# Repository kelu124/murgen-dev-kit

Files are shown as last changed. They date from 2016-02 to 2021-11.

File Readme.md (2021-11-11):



# The Murgen open-source ultrasound imaging dev-kit 

## What is this ?
 
Getting a home-made open-source ultrasound machine (dev-kit) up and running in your garage / hackerspace / fablab for less than 500$ (want the bolts and nuts of the murgen-based prototype ? Read a more complete [hardware Readme.md](/hardware/Readme.md) and in general the [murgen repo](https://github.com/kelu124/murgen-dev-kit/) ). 

For a full overview of the adventure, visit our [Hackaday page](https://hackaday.io/project/9281-murgen) =)

**For the full documentation of the overaching project, please visit our [full doc](https://kelu124.gitbooks.io/echomods/content/)**

## Getting the rough rough first image

We've got **our first ultrasound image with the murgen board** =) Not a baby, mind you, but at least an echo coming from a part of a fantom (condom filled with agar gel and tapioca balls) in front of the transducer. And we haven't tapped into the full capabilities of the board yet, so it can be improved! Enclosed, the picture of the same fantom, using a commercial, 100k$ ultrasound machine.

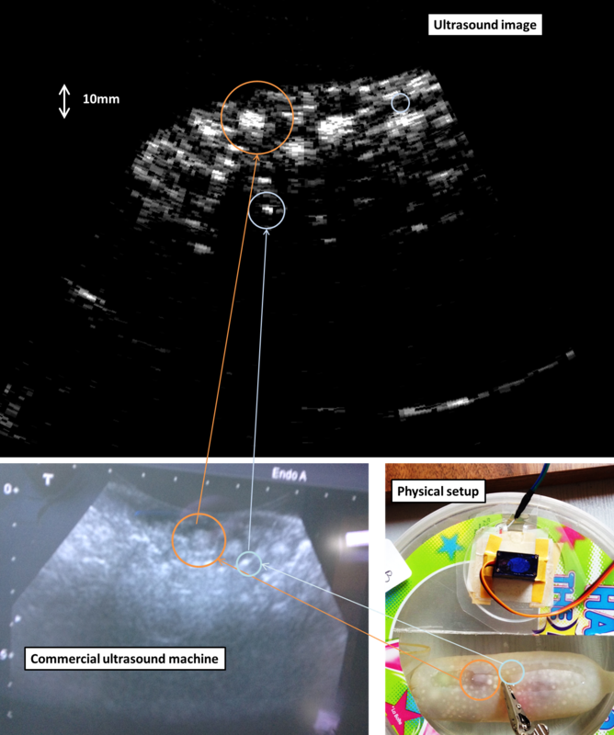
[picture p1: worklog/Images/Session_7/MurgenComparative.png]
A nice image


## Setting up a prototype

### Disclaimers

**Disclaimer #1**: though an engineer, this project is the first of its sort, we never did something related. Bear with us, and the discovery process – we’re happy to learn on the way =)

**Disclaimer #2**: ultrasound raises questions. In case you build a scanner, use caution and good sense!
**Disclaimer #3**: this project is not part of echopen.

### How-to start

Time to get some shopping done !

* Get a murgen dev-kit: 140€ in electronics + PCB. Or 100€ with the components to put on a breadboard =)
* Get a BitScope: 150€
* Get a transducer : 110€ for brand new adaptaed ones, ~100€ for one found on ebay and hacking it
* Get a Trinket Pro / Arduino : 10€
* Get some small electronics (breadboard, cables et al) : 20€
* Misc (Pizza, Beer, and a donation to Murgen): 15€

**_Total spent_: 400€ to 450€**

### Setup
#### Connections

* Connect the BitScope Chan A to Trinket Pin 11, and Chan B to Tests Points2 and 3.
* Connect the trinket pins 12 and 13 to a 5-to-3V convertor (or double invertor), then to the board USPP and USPN pins.
* Bring power to the board (GND, 5V, 3.3V) - the board uses ~150mA at 5V, so you can use a breadboard alim (see IMG_2413 below).

#### Hardware setup presentation

PhysicalSpace

### Software User’s Quick-Start Guide

Just Install the following:

* BitScope BitLib
* python math tools
* Install something to code arduino - ArduinoIDE ?
* Clone the [murgen repo](https://github.com/kelu124/murgen-dev-kit/) 

You're good to go !

### Learn more : the lab log

- [Session 1](/worklog/Session_1.md) : Powering the board, power use, first (bad) trigging and echoes (06 March 2016)
- [Session 2](/worklog/Session_2.md) : Non-controlled pulsing, inverters, better echoes (11 March 2016)
- [Session 3](/worklog/Session_3.md) : Getting controlled pulsing, but width not controlled (15 March 2016)
- [Session 4](/worklog/Session_4.md) : Width of the pulses is getting controlled =) (19 March 2016)
- [Session 4b](/worklog/Session_4b.md) : Simple data visualisation with BitScope (19 March 2016)
- [Session 5](/worklog/Session_5.md) : moving the transducer to get the first image (20 March 2016)
- [Session 6](/worklog/Session_6.md) : ***Getting a clinically usable image*** (28 March 2016)
- [Session 7](/worklog/Session_7.md) : Getting cleaner images - code improvements  (3 April 2016)
- [Session 8](/worklog/Session_8.md) : Comparing acquisition speeds (3 May 2016)
- [Session 9](/worklog/Session_9.md) : Playing with ATL10PV (3 July 2016)
- [A more complete hardware ReadMe](hardware/Readme.md) : Information, and more, with a focus on the electronic part of the project
- [A more complete software ReadMe](software/Readme.md) : Information, and more, with a focus on the code part of the project (arduino, python, and such)

## FAQ

### I want to get to run one

Where should I go? You can peruse a discussion/tutorial with a new user of the board [here](http://kelu124.github.io/murgen-dev-kit/).

### What do I find here?

A full official dev release, including:

* Terms of reference for the project
* Bibliography
* Detailed designed
* Source file for the electronic board
* Source for the Arduino controlling the board
* Source for acquisition, processing and storage of the images
* A full laboratory log

### Typical Application

Playing with a broken transducer in a haribo sweet box to see if you can hack ultrasound scanners.

### Software / Firmware Summary

Up to v1.0, we're still playing with the board, so there's not interface with the BBB.

However, there's a series of tools to play with the board, one of which being the bitscope, a bit more handy than the redpitaya, and though it is less precise, we do have less issues (trigging, memory, ...) with it.

### What is the timeline?

The murgen investigation had started in September 2015, and by the end of November, it had been activated again. 

### Find your way in the folders

 	murgen-dev-kit/				main repo
 	|-- hardware				hardware information on electronics and mecanics
 	|-- software				code to acquire, process and store ultrasound data
 	`-- worklogs				logs froms the lab: our path to a working ultrasound device

* You will find the CHANGES.TXT, CONTRIB.TXT and LICENSE.TXT at the root.
* Schematics are in the ***hardware\Altium\Schematics\PDF*** folder
* Gerbers in in the ***hardware\Gerbers*** folder of course
* Code for the acquisition using bitscope (at first ;) ) is in ***software/***.

# Remaining TODOs

The project's phase is coming to an end! Some ideas, lessons, stuff at our [NextSteps.md](/NextSteps.md)

* Playin with the PRUs, there's [some inspiration there](https://www.element14.com/community/community/designcenter/single-board-computers/next-gen_beaglebone/blog/2013/08/04/bbb--high-speed-data-acquisition-and-web-based-ui)
* There are 5 big projects listed on the [NextSteps.md](/NextSteps.md) document.

# Team

## Acknowledgement

* Thanks to Murgen, Sofian, Amit, Emmanuel, Florent, Bertrand & PHH, Mike in a way, list goes on !
* Thanks to Jerome, Farad, Vincent obviously
* Thanks to echOpen for the environment, wifi and coffee =)

# License

The Murgen project and its prototypes are open hardware, and working with open-hardware components.

Licensed under TAPR Open Hardware License (www.tapr.org/OHL)

Copyright Kelu124 (kelu124@gmail.com ) 2015-2018

[Source](/Readme.md)

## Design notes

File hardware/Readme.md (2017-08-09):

# The Murgen Project
_The hardware design process is fraught with pitfalls, from library component sketchiness, parts availability, erroneous data sheets, underestimates of complexity and long lead times. Designing good hardware on time, on budget and to specifications is like being in a knife fight. Hardware will cut you._

## What is this project?

Today, **we have achieved the electronic design of the kit and are having it made by a PCB Assembly** – someone to actually assemble the probe, and we're waiting for a first prod so that **we can physically test it with our in house transducer**.

That’s cool! And if you want to learn more (apart from this Readme), you can surf the internet and  :

- Read the the [Hackday Blog](https://hackaday.io/project/9281-murgen) of the fork !

### Results ?
#### Setup 

The working place

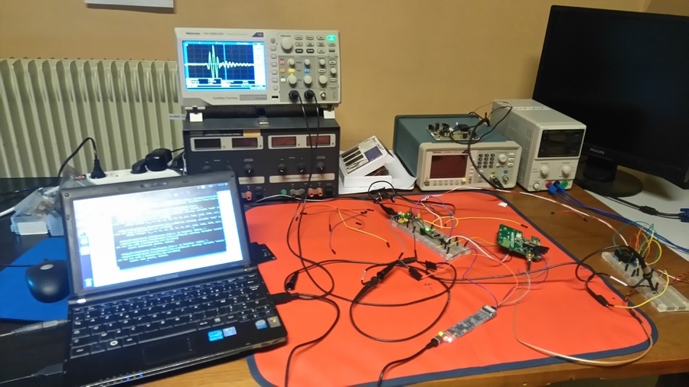
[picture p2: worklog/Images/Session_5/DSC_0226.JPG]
The assembled dev kit


#### Images

A first picture of our baby !

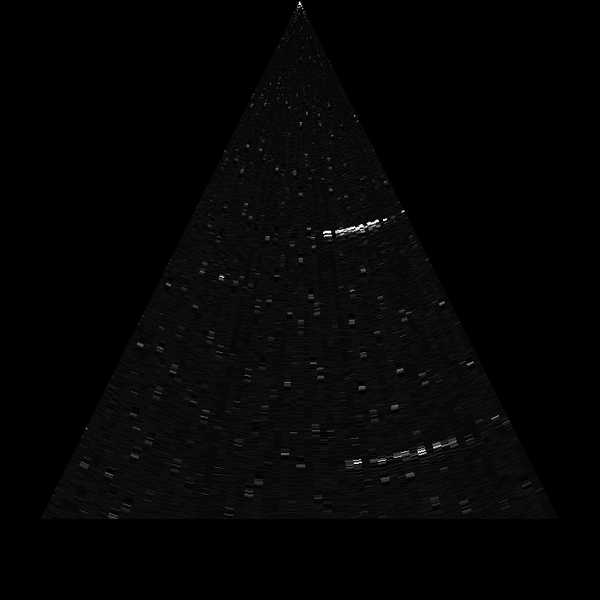
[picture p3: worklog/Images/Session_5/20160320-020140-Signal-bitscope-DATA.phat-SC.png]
An ultrasound image


### Disclaimers
**Disclaimer**: though an engineer, this project is the first of its sort, we never did something related. Bear with us, and the discovery process – we’re happy to learn on the way =)

**Disclaimer #2**: ultrasound raises questions. In case you build a scanner, use caution and good sense!
### Teaser
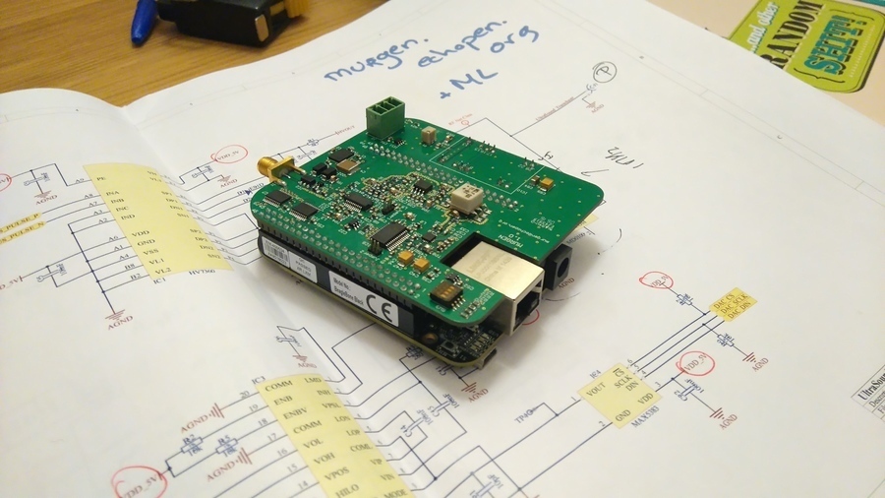
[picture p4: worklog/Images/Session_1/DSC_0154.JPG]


# Folders

    hardware/			main repo
    |-- Altium			the altium files for Murgen -- source files, opening with Altium Designer
    |-- BOM				that's ... well.. for the BOM
    |-- Gerbers			to build the cape
    |-- 3D				for the 3D files of the board	
    |-- tobo			simplified pulser
    `-- goblin			an alternative, in Eagle

You will also find the CHANGES.TXT, CONTRIB.TXT and LICENSE.TXT at the root.
	 
Schematics are in the ***Altium\Schematics\PDF*** folder
	 
# Project introduction

## Brief

**Disclaimer**: this brief ***does not*** rock. It is crappy, but, well, we live to learn.

In October 2015, we were working on a open-source ultrasound imaging device, and had started to get some result. However, we were facing a bottleneck that is data acquisition and transfer.

Roughly, the aim of the device is to excite a 3.5MHz piezo through a 100V or more, 0.2µs, signal to acquire a signal coming from the echoes.

Once it comes back from the transducer, one needs to cap it, amplify it, filter it, apply a time variable gain to the signal, have it get through a high speed ADC (40MHz at least), and serve it to the the processing unit (through PINs, SPI, USB ?), possibly with a CPLD/FPGA (or DSP / microcontroler ?) in between.

As the data we have should have at least 16 imgs / sec, with 64 lines, the rate shall be around 120Mb/s, and to avoid the data transfer bottleneck (see Estimating datarates), we were thinking of leverage the capacities of raspberry (or beaglebone) and such to have shields/capes that can be used and connect through SPI for example to the raspberry where raw data can be processed, and image can be going out, hence a lower rate.

## A bit more context

### The board

The board in itself is not a medical device. The board is a dev kit for the analog part that one could find in any ultrasound probe. It respects the functions and blocks one can find in basically any probe (pulser, TGC, ADC, ..). A main difference is that this board is designed for a single element, and provides so far only a minimal support for the mechanics behind image formation.

Having a single element allows for more space, less density, and to go straight to a regular, though relatively high-speed ADC.

### The Process

None of us had already done an electronic product, so the process in not that of an experienced team, and we're learning on all the fields: writing down an idea, analysing it, structuring it, develop the plans, build it, test it, build the software.. Rince and repeat.

The most challenging part, and somewhere the easiest, will be to allow anyone with little or no experience to replicate our efforts, and to build another copy of the board. Why is that so? With fresh eyes, that's easier to understand what the blocking points could be, what needs to be detailed, and how.

### Debug Sessions

#### Finding the short

The [notes are here](/hardware/murgen-1.0-short-issue.md) (the murgen-1.0-short-issue.md file). We found the bug, two main issues are to be corrected on board v1.1:

* A short on the ADL5511
* The RECOM has to be mounted upside down, as the pin layout were inverted during the design stage

#### Playing with the board

The notes are here, stemming from the work sessions with the board:

- [Session 1](/worklog/Session_1.md) : Powering the board, power use, first (bad) trigging and echoes (06 March 2016)
- [Session 2](/worklog/Session_2.md) : Non-controlled pulsing, inverters, better echoes (11 March 2016)
- [Session 3](/worklog/Session_3.md) : Getting controlled pulsing, but width not controlled (15 March 2016)
- [Session 4](/worklog/Session_4.md) : Width of the pulses is getting controlled =) (19 March 2016)
- [Session 4b](/worklog/Session_4b.md) : Simple data visualisation with BitScope (19 March 2016)
- [Session 5](/worklog/Session_5.md) : moving the transducer to get the first image (20 March 2016)
- [Session 6](/worklog/Session_6.md) : ***Getting a clinically usable image*** (28 March 2016)
- [Session 7](/worklog/Session_7.md) : Getting cleaner images - code improvements  (3 April 2016)
- [Session 8](/worklog/Session_8.md) : Comparing acquisition speeds (3 May 2016)
- [Session 9](/worklog/Session_9.md) : Playing with ATL10PV (3 July 2016)
- [A more complete hardware ReadMe](hardware/Readme.md) : Information, and more, with a focus on the electronic part of the project
- [A more complete software ReadMe](software/Readme.md) : Information, and more, with a focus on the code part of the project (arduino, python, and such)

## Preliminary questions

### Why are we making this?

Because it’s fun, it the first step towards medical open hardware based on ultrasounds, so it’s an element for echOpen !
And because existing hardware doesn’t come in for low-cost, rough uses.

### Who is this for?

This element, comprised of the analog part of ultrasound imaging processing, is aiming hackers, makers, … all who can have fun prototyping a low-cost ultrasound device.

### How will this be used?

This shall be used in conjunction with the mechanical unit (motor, encoder, transducer), and plugged into a small processing unit (aka Raspberry, or BeagleBOne Black for exemple)

### What features does it need to have (now)?

Be able to emit a ultrasound pulse at high voltage, and receive a signal, clean it, detect the envelop and ADC it.

### What features does it need to have (later)?

Shifting envelope detection to software once we’re sure the processing works at “low” rates.

### What are the legacy requirements?

Nothing yet, except a couple of constraints on the use of the tool.

### Who’s going to build this?

Makers, doers, academics, … can use this. But we’d be happy to go with a PCB assembler at first!

### How many do we want to make?

At first, a couple, to prototype it. Once prototyped, this board could be in the hundreds.

### What is the timeline?

**The objective is to get a first functional prototype by February 2015.**

### What are the Goblin and Tobo stuff ?

Those are two alternatives to murgen, in the sense that components may not be the same for goblin, and that tobo is a mini-murgen, limited to the pulser. Goblin is a simpler version, a two-layer one, but we'll need funds to test this one out =)

## Requirements to build the board

### BOM

In the BOM folder !

### At the fab

#### PCB 

A 4-layer PCB.. not so cheap, but at the same time..

#### Fab

Lots around... choose what you want =)

#### Links

PCB Maker:

- seeedstudio.com
- PCBshopper.com

PCBA abroad :

- myropcb
- nortechsys
- SeeedStudio only north america

PCBA in france:

- Quad Ind
- PCB-Pool
- EdgeFlex

### Costs

With the french fab we're working with, costs sum to 160e, and they are split as follows, prices being without taxes:

- PCB : 7.34e (but there are overcosts to produce the masks, ...)
- Components : 143.5e and T1-6T-KK81+ (sold by 10): 9.34 each, but can come down to 140e with some volume.

In this case, assembly is close to 120e.

## Technically

### Principles of echography

Basically, echography means plotting echoes. It means we have to create a sound pulse (2), use a good sensor (2), find a way to transform a 1D signal to a 2D image (3), listen to the echoes coming back, cleaning them and  processing them to create an image the way a bat would do (4), and to transmit them to a display (5). 5 steps.

The present project aims at taking care of (1), (4) and (5) - meaning amm electronics related to the analogic part of the imaging.

### Narrative of the flow

Since we're using a single sensor (not an array of sensor, as those are used in "regular" machines), we don't have the Beamforming parts. The 
sensor is similar to a speaker, in the sense that it can be used to generate an acoustic signal from electricity, and vice versa. The flow is therefore as follows:

- A pulse generator generates a high negative voltage pulse, which is as low as possible and to excite the transducer (or crystal), which will resonate at his central frequency. In our case, this is 3.5MHz, but that depends on the transducer being used.
- A signal will come back through the echoes, the reverberation of the acoustic waves on "obstacles", exciting the transducer, having it generate an electric signal.
- This will be prepared by a switch. Indeed, the signal needs to be separated from the excitation. Excitation being at -150V, the signal coming back will be in mV - and it needs to be isolated.
- The signal usually goes through a LNA - low noise amplifier - to be amplified
- then it's processed by a TGC to compensate for signal attenuation. Indeed, the deeper the echoes come back from, the more attenuated they are, and this needs to be corrected.
- An AAF (Anti-Alias Filte) can be put in between, and in the case of the first Murgen release, we also include an enveloppe detection: indeed, echoes are signals that are coming from a couple of ultrasound periods reflected on interfaces, and what interests us is not (at first) the signal itself, rather the enveloppe of it.
- The "cleaned" signal goes through an ADC to be digitalized
- this is output to buffers, in our case to protect the BBB GPIOs.

### Data rates and key figures

- We're aiming at **128 lines/image** - that may be enough at first 
- at **16 imgs/s**, that's 2048 lines/s
    - That's 488us per line (for everything: 
- Let's image no further than 15.77cm deep.. Why? Because :
    -(15.77 cm x 2) / (154000 cm/s) = 204.805 us 
    -that's 1024 pts at 5MHz
    -That's **204.805 us** per line
    -That's **283.5 us** of idle time - kept for processing, and whatnots
- Final image is therefore **128*1024 px**
    -1024 pts for 15.77cm is 6.49px / mm
    -That's also 2.1Msps on average or 24Mbit/s.. borderline for data transfer on certain systems.

## Discussions

The bottleneck may lie in the data transfers...

### Data rates and Data bus

- 151202: QuadSPI through a dedicated microcontroleur?
- 151201: At 5Msps, 12 bits, shall we use SPI or parallel? 
- 151201: SPI is managed through hardware... parallel, not. Has to be managed from soft. Can be an issue for real time, and to avoid loosing samples.
- 151130: Rather be going onto SPI : QuadSPI? Is that managed by the RPi? Common amongst ADCs ?
- 151207: For high speed data acquisition: about 120Mbits/sec: No SPI port will support such speed…. Only the  Quad version… we can use USB 2.0 HS for such huge movement.  A FPGA or FPGA/RISC MPU combination can be the best  solution. Later, once on RPI, the data can be handled. But for so  perfect measurement of times, and value, only a DSP it’s not enough.  

### Signal detection

- 151129: LTC5507ES6 to filter ? A rajouter!

### ADC and DAC

- 151130: Better ADC at LTC2315-12
- AD7356 (ual, 12-bit, high speed, low power, successive  approximation ADC that operates from a single 2.5 V power  supply and features throughput rates up to 5 MSPS.  
- DAC: a simple DAC i2c 

### Different setups

- 151202: A DSP may be sufficient for our needs: is that the case? 
- 151203: Proposed setup
    - Using a a Main controller - STM32F407 + USB High speed PHY ?? 
    - Analog frontend :  1/4 of AD8264 as LNA and VGA + AD9236 ADC. TGC  can be controlled by internal STM32 DAC - that's max 100-point TGC  calibration curve.  The ADC then could be connected to DCMI interface of  STM32.
    - Transmitter: could be HV Pulser and the TR switch - microchip HV7360 + MD0100,  STHV 748 
- 151209: In  looking at the issue, I think that DSP can be implemented. Of  course,  that comes with the sourcing and a bit of programming, but it  should  work and provide some flexibility. 
- 151112: 
     - it'd be interesting to keep a 100M s/s sampling rate.  
    - wouldn't recommend MD1210 and TC2320 from supertex for the pulse  part. Those have a recovery time that is quite long, and can get easily  damaged - not to mention that they may be obsolete.  
    - Wouldn't recommend two VGAs ... difficult to control, with a high risk of saturation. 

### 151201 : Electronics for all in one chips: AFE (Analog front end)

#### Rationale 

It appears that compoonent MAX2082 from  Maxim's could be a great choice because it integrates everything in one chip (Analog Front End, Pulser, TCG (ou AVG pour eux), T/R Switch, ADC, Filtrage) - maybe better exists ?
Note : Pre-existing chips are 8-channels.

##### Resources

- MAX2082 - Maxim  (Pulser +/- 105 V), TCG (ou VGA) , ADC 50 MSPS and filtering (63$ a piece starting at 1000 units)
https://www.maximintegrated.com/en/products/analog/data-converters/analog-front-end-ics/MAX2082.html
- Several Maxim's Analog Front end  : https://para.maximintegrated.com/en/results.mvp?fam=us_afe
- Pulser - 90 V (16$ a piece starting at 1000 units) : http://www.st.com/web/en/news/n3553d
- A  Texas Instrument Dev Kit : http://www.ti.com/tool/tx-sdk-v1
- Several other Ultrasound Analog Front end (all are 8 channels):  
    - http://www.analog.com/media/en/news-marketing-collateral/product-highlight/AD927x-AD967x-Octal-Ultrasound-AFE-Product-Family.pdf
    - http://www.analog.com/en/products/landing-pages/001/integrated-afe-contains-8-ultrasound-rcv-channels.html
    - http://www.analog.com/en/products/analog-to-digital-converters/ad-converters/ad9675.html
    - http://www.digikey.com/web%20export/supplier%20content/TI_296/mkt/health/afe5809.pdf?redirected=1
    - http://www.ti.com/product/afe5801
- Ultrasound Receiver module (32 channel) (maybe not so cheap) : http://www.cephasonics.com/product/ultrasound-receiver-modules-csm913233

#### Need of a FPGA ?

According to articles and reading, it seems like it will be delicate to proceed without a FPGA for data processing. All "Reference Design" sheets I've read do have a FPGA, or a DSP.... because signals to be processeed are IMHO too fast for a µC.

#### Microcontroler

- Microchip - a µC PIC24FJ128GC010 - ADC, 12 bit, 10 MSPS : http://www.microchip.com/wwwproducts/Devices.aspx?product=PIC24FJ128GC010
- and its dev board at 100$: http://www.microchip.com/Developmenttools/ProductDetails.aspx?PartNO=DM240015
- ST ant its ADC 12 bit 5 MSPS  µC STM32F334R8: http://www.st.com/web/en/catalog/mmc/FM141/SC1169/SS1576/LN1531/PF258875#
- with its dev board at 10 € : http://fr.farnell.com/stmicroelectronics/nucleo-f334r8/carte-dev-32-bits-stm32f334r8/dp/2424210
- Analog Device has a reference list µC  : 
http://www.analog.com/en/products/processors-dsp/analog-microcontrollers/8052-core-products.html
- At analog device, the best seems to be ADSP-CM40XF with a 16 bit ADC at 2,3 MSPS: http://www.analog.com/en/products/processors-dsp/cm4xx-mixed-signal-control-processors/adsp-cm403f.html#product-overview  and its 2 dev boards:
 - http://fr.farnell.com/analog-devices/adzs-cm408f-ezlite/kit-d-eval-ez-kit-lite-adsp-cm408f/dp/2367988?CMP=GRHS-1000059
 - http://fr.farnell.com/analog-devices/adzs-cm403f-ezlite/kit-d-eval-ez-kit-lite-adsp-cm403f/dp/2367987?CMP=GRHS-1000059
- I also found some MCU with an internal ADC and a good rate wich seems interesting : http://www.analog.com/en/products/processors-dsp/analog-microcontrollers/8052-core-products.html and http://www.microchip.com/Developmenttools/ProductDetails.aspx?PartNO=DM240015

### Forks

#### Constraints

- 151124: The tech milestone was on Nov 24th '15 -  and we need to have something by mid Feb' 16.

#### YDO ideas

- 151125: I'm pretty sure that it's impossible that a microcontroler, raspberry or beaglebone can process this data at a speed above 5Msps.  Most of ADCs have a SPI interface, with a 12-bit ADC at 5Msps we'd need a SPI at more than 60Mbps - not everything can do ! In such a case, a DSP or a FPGA is a must-have.

#### LJO/FKA cape

- 151124: let's play with the BBB PRU's and develop a analog+ADC cape.

### HV Supply

HV-supply is going to introduce noise in the circuit.. therefore, a home-made booster was not selected, especially when going at 100V+. We had to options to consider:

- Using a **MAX1711** in [Jatin Sharma thesis](https://www.duo.uio.no/handle/10852/47813), he goes from 12V to 180V. Gerbers and schematics are included in his master).  The board was separated from the rest of the design, to avoid any pickup/noise.
- We have tried the **R05-100B** - a tad more simple, and based on 5V, so easier for us (5V -> 120V).  Schematics are simple, introducing only a couple of capacities.

### Electronics

So far, the key issue is a compromise in terms of data output. It's interesting to see how to interface such data rates to a processing and display unit.

### Setup

#### Jumper 1

This one represents the fixed Gain for the TGC. An extra 18 dB is always handy!

#### Jumper 2

todo

#### ADC Clock:

The 4 options switch allows for a sampling frequency range of choices:

|  R1 |  R2 |  R3 |  R4 | Rset Value | Clock Frequency |
|:---:|:---:|:---:|:---:|:----------:|:---------------:|
|  1  |  2  |  3  |  4  |     Ohm    |      [MHz]      |
| OFF | OFF | OFF | OFF |   Invalid  |     Invalid     |
| OFF | OFF | OFF |  ON |  100000,0  |       1,0       |
| OFF | OFF |  ON | OFF |   40200,0  |       2,5       |
| OFF | OFF |  ON |  ON |   28673,3  |       3,5       |
| OFF |  ON | OFF | OFF |   27400,0  |       3,6       |
| OFF |  ON | OFF |  ON |   21507,1  |       4,6       |
| OFF |  ON |  ON | OFF |   16294,1  |       6,1       |
| OFF |  ON |  ON |  ON |   14011,1  |       7,1       |
|  ON | OFF | OFF | OFF |   20000,0  |       5,0       |
|  ON | OFF | OFF |  ON |   16666,7  |       6,0       |
|  ON | OFF |  ON | OFF |   13355,5  |       7,5       |
|  ON | OFF |  ON |  ON |   11781,9  |       8,5       |
|  ON |  ON | OFF | OFF |   11561,2  |       8,6       |
|  ON |  ON | OFF |  ON |   10363,1  |       9,6       |
|  ON |  ON |  ON | OFF |   8978,9   |       11,1      |
|  ON |  ON |  ON |  ON |   8239,1   |       12,1      |

## Parts, ICs selection (and critical specs)
 
### HV7360:  High Speed, ±100V 2.5A, Two or Three Level Ultrasound Pulser

* High density integration AC coupled pulser
* 0 to ±100V output voltage
* ±2.5A source and sink minimum pulse current
* Up to 35MHz operating frequency
* 2.0ns matched delay times
* 2.5, 3.3 or 5.0V CMOS logic interface
* Low power consumption and very simple to use

HV7360 is a high voltage, high-speed, pulse generator with built-in, fast return to zero damping FETs. This high voltage and high-speed integrated circuit is designed for portable medical ultrasound image devices, but can also can be used for NDT and test equipment applications.

The HV7360 consists of a controller logic interface circuit, level translators, AC coupled MOSFET gate drivers and high voltage and high current P-channel and N-channel MOSFETs as the output stage. The peak output currents of each channel are guaranteed to be over ±2.5A with up to ±100V of pulse swing. The AC coupling topology for the gate drivers not only saves two floating voltage supplies, it also makes the PCB layout easier.

### Protection: MD0100 Datasheet - HV Protection T/R Switch

* Up to ±100V input voltage protection
* Low on resistance - 15O typical
* Fast switching speed
* Effectively, a simple two terminal device
* No external supplies needed

MD0100 is a high voltage, two terminal, bi-directional, current-limiting protection device. The two terminals are interchangeable. It is designed to protect a low noise receiver from the high voltage transmit pulses in ultrasound applications and is commonly referred to as a T/R (transmit and receive) switch. The MD0100 can be considered as a normally closed switch with a typical switching resistance of 15O that allows small signals to pass.

Once the voltage drop across the two terminals exceeds a nominal value of ±2.0V, the device will start to turn off. In the off state, the MD0100 can withstand up to ±100V across its terminals.

A small amount of current, typical of 200µA, is allowed to flow through.
 
### TGC : AD8331 (Single VGA with Ultralow Noise Preamplifier and Programmable RIN)

* Ultralow noise preamplifier
* 3 dB bandwidth: 120 MHz
* Low power: 125 mW/channel
* Wide gain range with programmable postamp (-4.5 dB to +43.5 dB in LO gain mode, 7.5 dB to 55.5 dB in HI gain mode) – we can use this with the corresponding on-board jumper
* Low output-referred noise: 48 nV/vHz typical
* Active input impedance matching
* Optimized for 10-bit/12-bit ADCs : perfect for us
* Selectable output clamping level
* Single 5 V supply operation : ideal for a 5V board supply!

The AD8331 is a single channel, ultralow noise, linear-in-dB, variable gain amplifier (VGA). Optimized for ultrasound systems, it is usable as a low noise variable gain element at frequencies up to 120 MHz.

Included is an ultralow noise preamplifier (LNA), an X-AMP® VGA with 48 dB of gain range, and a selectable gain postamplifier with adjustable output limiting. The LNA gain is 19 dB with a single-ended input and differential outputs. Using a single resistor, the LNA input impedance can be adjusted to match a signal source without compromising noise performance.

The 48 dB gain range of the VGA makes these devices suitable for a variety of applications. Excellent bandwidth uniformity is maintained across the entire range. The gain control interface provides precise linear-in-dB scaling of 50 dB/V for control voltages between 40 mV and 1 V. Factory trim ensures excellent part-to-part and channel-to-channel gain matching. Differential signal paths result in superb second- and third-order distortion performance and low crosstalk.

### TGC  Control : SPI DAC : MAX5383

Controls the TGC
* 8-Bit Resolution in a Miniature 6-Pin SOT23 Package
* Less than 1µA Shutdown Mode
* Low-Glitch Power-On Reset to Zero DAC Output
* 3-Wire SPI/QSPI/MICROWIRE-Compatible Interface : perfect for a SPI interface
* Low 230µA (max) Supply Current

The MAX5383 low-cost, 8-bit digital-to-analog converters (DACs) in miniature 6-pin SOT23 packages have a simple 3-wire, SPI™/QSPI™/MICROWIRE™-compatible serial interface that operates up to 10MHz. The MAX5383 has an internal +2V reference and operates from a +2.7V to +3.6V supply.

The MAX5383 require an extremely low supply current of only 150µA (typ) and provide a buffered voltage output. These devices power up at zero code and remain there until a new code is written to the DAC registers. This provides additional safety for applications that drive valves or other transducers that need to be off on power-up. The MAX5383 include a 1µA, low-power shutdown mode that features software-selectable output loads of 1kO, 100kO, or 1MO to ground.

### Analog envelop detection: ADL5511 - DC to 6 GHz ENVELOPE AND TruPwr™ RMS Detector

* Envelope tracking RF detector with output proportional to input voltage
* No balun or external tuning required
* Input power dynamic range of 47 dB
* Input frequency range from dc to 6 GHz
* 130 MHz envelope bandwidth
* Envelope delay: 2 ns
* Single-supply operation: 4.75 V to 5.25 V

The ADL5511 is an RF envelope and TruPwr™ rms detector. The envelope output voltage is presented as a voltage that is proportional to the envelope of the input signal. The rms output voltage is independent of the peak-to-average ratio of the input signal.
The rms output is a linear-in-V/V voltage with a conversion gain of 1.9 V/V rms at 900 MHz. The envelope output has a conversion gain of 1.46 V/V at 900 MHz and is referenced to an internal 1.1 V reference voltage, which is available on the EREF pin.
The ADL5511 can operate from dc to 6 GHz on signals with envelope bandwidths up to 130 MHz.

### ADC : AD9220 - Complete 12-Bit, 10.0 MSPS Monolithic A/D Converter

* Monolithic 12-Bit A/D Converter Product Family
* Flexible Sampling Rates: 1.5 MSPS, 3.0 MSPS, and 10 MSPS
* Single +5 V Supply
* Out-of-Range Indicator
* 28-SOIC and 28-SSOP

The AD9221/AD9223/AD9220 combine a low cost, high speed single-CMOS process and a novel architecture to achieve the resolution and speed of existing hybrid and monolithic implementations at a fraction of the power consumption and cost. Each device is a complete, monolithic ADC with an on-chip, high performance, low noise sample-and-hold amplifier and programmable voltage reference. An external reference can also be chosen to suit the dc accuracy and temperature drift requirements of the application. The devices use a multistage differential pipelined architecture with digital output error correction logic to provide 12-bit accuracy at the specified data rates and to guarantee no missing codes over the full operating temperature range.

The input of the AD9221/AD9223/AD9220 is highly flexible, allowing for easy interfacing to imaging, communications, medical, and data-acquisition systems. A truly differential input structure allows for both single-ended and differential input sample-interfaces of varying input spans. The sample-and-hold (SHA) amplifier is equally suited for both multiplexed systems that switch full-scale voltage levels in successive channels as well as sampling single-channel inputs at frequencies up to and beyond the Nyquist rate. Also, the AD9221/AD9223/AD9220 is well suited for communication systems employing IF Down Conversion since the SHA in the differential input mode can achieve excellent dynamic performance far beyond its specified Nyquist frequency2.

A single clock input is used to control all internal conversion The digital output data is presented in straight binary format. An out-of-range (OTR) signal indicates an flow condition which can be used with the most significant bit to determine low or high overflow.
 
### Buffers: 74AC541MTC

* Signal isolation is of high value for measurements at this precision (12bit)

The 74AC541 and 74ACT541 are octal buffer/line drivers designed to be employed as memory and address drivers, clock drivers and bus oriented transmitter/ receivers.
 
# Using the Murgen board

## Software / Firmware Summary

Up to v1.0, we're still playing with the board, so there's not interface with the BBB.

However, there's a series of tools to play with the board, one of which being the bitscope, a bit more handy than the redpitaya, and though it is less precise, we do have less issues (trigging, memory, ...) with it.

## Typical Application

Playing with a broken transducer in a haribo sweet box to see if you can hack ultrasounds.

## User’s Quick-Start Guide

- Install 
    - BitScope BitLib
    - python math tools
    - something to code arduino
- Clone this repo

You're good to go !

# Others

## Goodies 
Check out [oldTobo](/hardware/tobo/) -- an stand-alone pulser/receiver board and [oldGoblin](/hardware/goblin/) for an alternative version.

## People ! 

### Acknowledgement

* Thanks to echOpen =)
* Thanks to Jerome, Farad, Vincent obviously
* Murgen, Sofian, Amit, Emmanuel, Florent, Bertrand & PHH, Mike in a way, list goes on !

# License

Licensed under TAPR Open Hardware License (www.tapr.org/OHL)

Copyright Kelu124 (kelu124@gmail.com ) 2015-2016

# Bibliography

## FPGA-related bibliography

- Structuring a whole ultrasound system on a board: an excellent thesis from P. Levesques (Kyvox),  File:2011 PhilippeLevesque.pdf. 
- A first corresponding article: File:Real-Time Hand-Held Ultrasound Medical-Imaging Device Based on a New Digital Quadrature Demodulation Processor.pdf
- the second corresponding article: File:Novel Low-Power Ultrasound Digital Preprocessing Architecture for Wireless Display.pdf
- Hardware-Software Partitioning of Digital Signal Processing in Ultrasound Medical Devices a Case Study : File:Hardware-Software Partitioning of US probes.pdf
 - File:A Single FPGA-Based Portable Ultrasound Imaging System for Point-of-Care Applications.pdf
 - File:Low-Cost, High-Speed Back-End Processing System for High-Frequency Ultrasound B-Mode Imaging.pdf
- Extremely interesting too,  iPHONE ULTRASOUND By Jonathan Adam, Adam Keen, Dean Santarinala  and File:project2_presentation.pdf their presentation

## Key general articles (base of inspiration for our dear Emile)

- A single monoelement, low-cost ophtalmic probe using a piezo motor : File:Carotenuto ophtalmic prob.pdf : an excellent article. 
- A single monoelement, low-cost USB probe using a CPLD + microcontroller File:Richard low cost probe.pdf, including a great diagram block of the USB probe 
- Saijo USB work : Development of an ultra-portable echo device connected to USB port : Resource: File:2004 Development of an ultra-portable echo device connected to USB port.pdf
- A Software-Based Ultrasound System for Medical Diagnosis by Samir Ram Thadani File:1997 These MIT Thadani.pdf : an excellent introduction the overall design of a US probe design dating back from 1997. 
- Data processing and transfer in echography : File:Design of an Open-Architecture Ultrasound Acquisition System for Real-Time Processing and Control.pdf
- Transducer parameters: File:A focussed transducer-scatterer model for ultrasonic reference st.pdf

## Other

- Projet étudiant, réalisation d'un échographe de poche pour Iphone (très intéressant et très instructif...) : https://courses.engr.illinois.edu/ece445/getfile.asp?id=5167
- White paper de Xilinx : portable ultrasound system : http://www.xilinx.com/support/documentation/white_papers/wp378-Xilinx-in-Portable-Ultrasound.pdf
- Quelques Notes d'applications intéressantes de chez Maxim's :
https://www.maximintegrated.com/en/app-notes/index.mvp/id/5765
 https://www.maximintegrated.com/en/app-notes/index.mvp/id/5553
- Note d'application de chez ST sur "Ultrasound Imaging" :
 - http://www.st.com/web/en/catalog/apps/SE410/AS430/AC404
 - http://www.st.com/web/en/catalog/apps/SE410/AS430/AC404#
- Pulser TI avec Applcation Note d'une solution complète avec des composants TI :
 - http://www.ti.com.cn/cn/lit/ds/symlink/lm96550.pdf

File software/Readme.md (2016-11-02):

# Software Readme (Bitscope Version)

## Contents of the folder 

### Some files

* All example files are compressed and thumbs created in [the example folder](/software/examples/Readme.md)
* For the convention in files format, [the data files specs are in](/software/examples/Specs.md)

### Some software

* AcquireImage.py acquires the images, stores them in pairs of log files
* CreateImage.py creates the .data file from the log files
* CreateCSV.py creates the .csv file from the log files
* CreateSC.py creates the .png files (Scan Conversion) using a nearest neighbour algorithm, from the .data files
* CreateSC-4T.py creates the .png files (Scan Conversion) using the 4 nearest neighbours to determine the pixel value, from the .data files
* TrinketProCode is the code for the Arduino Trinket Pro.
* BatchImage is a shell script to automate the creation of images properly

### Some files
* The examples.tar.bz2 contains quite a lot of raw images, to be processed by CreateImage.py . There should be around 200Mo of raw images packed in this 4Mo archive.
* The [examples](/software/examples/) repository, and its [Readme](/software/examples/Readme.md),  contains some raw images, along with a table, and the [Specs](/software/examples/Specs.md)) for the data format.
* There's an additional folder for CSV images at [examples](/software/examples_csv/)

# Installing BitScope

## Setting up bitscope tools for Ubuntu, using BS05 (Bitscope Micro)	

1. Installation : install all deb/ .deb files (dpkg -i install_files/*.deb), starting with bitscope-link.
2. Follow the https://www.raspberrypi.org/forums/viewtopic.php?f=32&t=122636 instructions

```
 $ sudo unzip python-bindings-2.0-DC01L.zip -d /usr/share/doc/bitscope-library/examples/python/
 $ cd /usr/share/doc/bitscope-library/examples/python/
 $ cd /usr/share/doc/bitscope-library/examples/python/python-bindings-2.0-DC01L/
 $ sudo python setup-bitlib.py install
```
Compilation fails? To do that we discover that we should do this:
```
 $ sudo BASECFLAGS="" OPT="" CFLAGS="-O3" python setup-bitlib.py install
```
This should work and you should see:
```
 $ python test-bitlib.py 
 Starting: Attempting to open one device...
  Library: 2.0 FE26B (Python DC01L)
     Link: USB:/dev/ttyUSB0
 BitScope: BS000501 (YK26VX18)
 Channels: 10 (2 analog + 8 logic)
    Modes: FAST DUAL MIXED LOGIC STREAM
  Capture: 12288 @ 40000000Hz = 0.000307s (LOGIC)
   Offset: +2.917V to -6.217V
      POD:  9.20V  5.20V  3.50V  1.10V
  Data(5): 1.725000, 1.725000, 1.760937, 1.760937, 1.725000
 Finished: Library closed, resources released.
```

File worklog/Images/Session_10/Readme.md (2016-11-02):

## Testing the ATL3 probe

8h and ... minutes give:

* 37: end of the aquarium (motor: 2.3V)
* 38: itoo
* 39: deeper

* 40: Motor at 5.30V (170mA)
* 41: Motor at 10.3V (300mA)

* 46: Self (stomach)

* 49: bottle of US gel (2.3V) along its axe
* 50: itoo, perpandicular to the bottle

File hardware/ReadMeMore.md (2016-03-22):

# The Murgen Project
_The hardware design process is fraught with pitfalls, from library component sketchiness, parts availability, erroneous data sheets, underestimates of complexity and long lead times. Designing good hardware on time, on budget and to specifications is like being in a knife fight. Hardware will cut you._

## What is this project?

This project is born from a fork from the [echOpen](http://www.echopen.org) project (which aims at providing a low cost, open source ultrasound tool for doctors), with a specific target of **providing a technological kit to allow scientists, academics, hackers, makers or OSH fans to hack their way to ultrasound imaging**.

Today, **we have achieved the electronic design of the kit and are having it made by a PCB Assembly** – someone to actually assemble the probe, and we're waiting for a first prod so that **we can physically test it with our in house transducer**.

That’s cool! And if you want to learn more (apart from this Readme), you can surf the internet and  :

- Read the the [Hackday Blog](https://hackaday.io/project/9281-murgen) of the fork !
- Explore [echOpen’s general wiki](http://www.echopen.org)
- Suscribe to the mailing list at all@murgen.echopen.org
- Or wander around the rest of echOpen's [GitHub repos](http://github.com/echopen)

### Results ?
#### Setup 

The working place

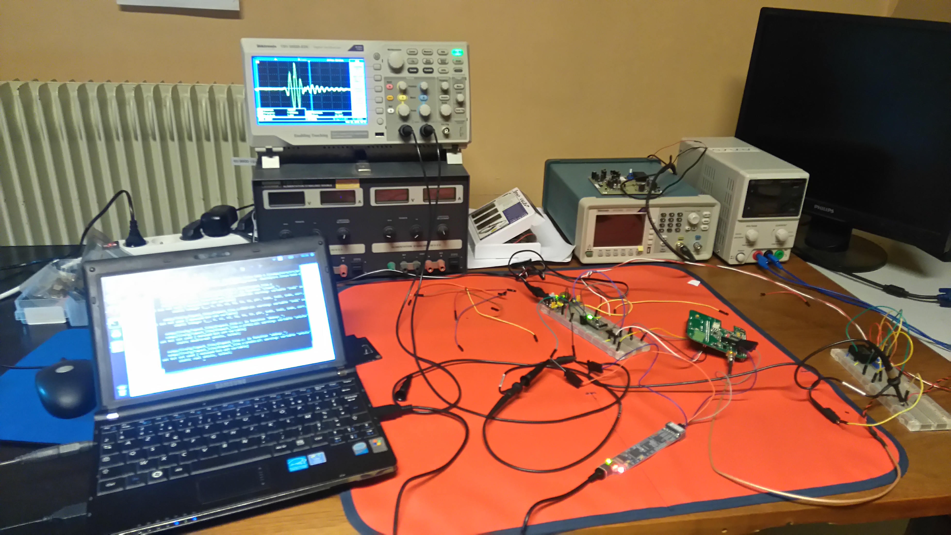
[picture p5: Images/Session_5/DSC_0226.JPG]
The assembled dev kit


#### Images

A first picture of our baby !

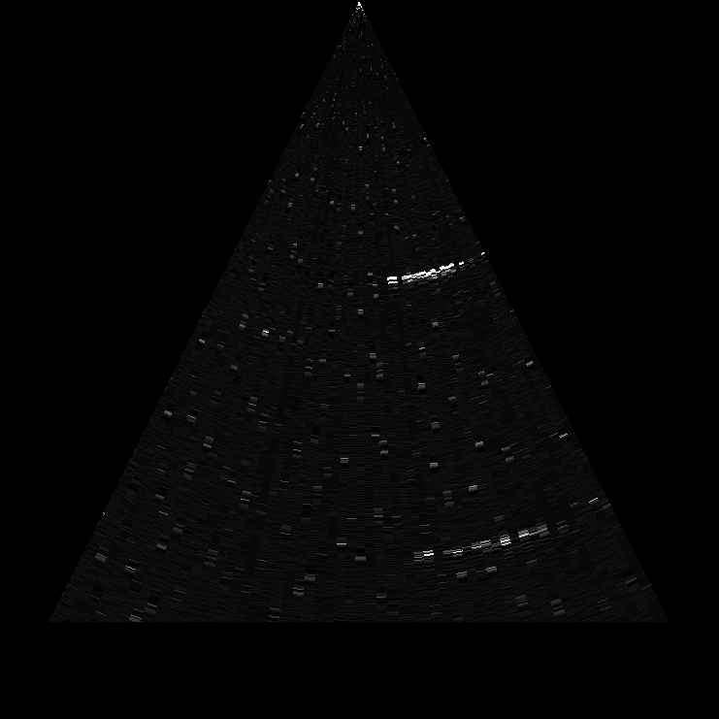
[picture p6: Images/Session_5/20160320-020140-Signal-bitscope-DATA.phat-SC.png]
An ultrasound image


### Disclaimers
**Disclaimer**: though an engineer, this project is the first of its sort, we never did something related. Bear with us, and the discovery process – we’re happy to learn on the way =)

**Disclaimer #2**: ultrasound raises questions. In case you build a scanner, use caution and good sense!
### Teaser
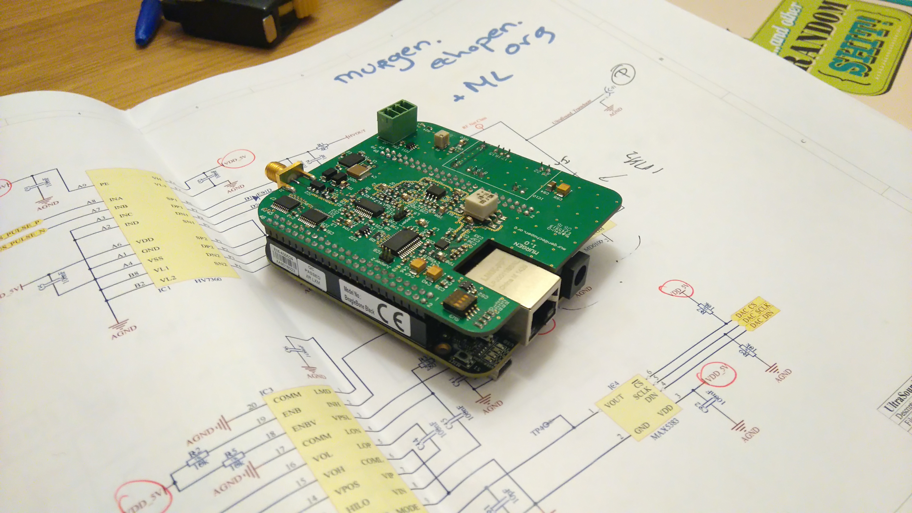
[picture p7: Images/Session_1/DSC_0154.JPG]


# Folders

     murgen-dev-kit/			         		main repo
	 |-- Altium						the altium files for Murgen -- source files, opening with Altium Designer
	 |-- BOM						that's ... well.. for the BOM
	 |-- Gerbers						to build the cape
	 |-- bitscope						to play with bitscope acquisition
	 |-- 3D							for the 3D files of the board	
	 |-- tobo					 	simplified pulser
	 |-- goblin						an alternative, in Eagle
         `-- Images						for documentation

You will also find the CHANGES.TXT, CONTRIB.TXT and LICENSE.TXT at the root.
	 
Schematics are in the ***Altium\Schematics\PDF*** folder
	 
# Project introduction
## Brief
**Disclaimer**: this brief ***does not*** rock. It is crappy, but, well, we live to learn.

In October 2015, we were working on a open-source ultrasound imaging device, and had started to get some result. However, we were facing a bottleneck that is data acquisition and transfer.

Roughly, the aim of the device is to excite a 3.5MHz piezo through a 100V or more, 0.2µs, signal to acquire a signal coming from the echoes.

Once it comes back from the transducer, one needs to cap it, amplify it, filter it, apply a time variable gain to the signal, have it get through a high speed ADC (40MHz at least), and serve it to the the processing unit (through PINs, SPI, USB ?), possibly with a CPLD/FPGA (or DSP / microcontroler ?) in between.

As the data we have should have at least 16 imgs / sec, with 64 lines, the rate shall be around 120Mb/s, and to avoid the data transfer bottleneck (see Estimating datarates), we were thinking of leverage the capacities of raspberry (or beaglebone) and such to have shields/capes that can be used and connect through SPI for example to the raspberry where raw data can be processed, and image can be going out, hence a lower rate.

More could be read from [echOpen's challenge](http://echopen.org/index.php?title=Challenge:_the_echOpen_shield) on the wiki.

## What is echOpen ?
echopen  is an association who wants to update the stethoscope resting around the neck of doctors, using an open-source, low-cost take at echography - and to provide the academic and hackers community with a ultrasound testing platform, doctors with an echo-stethoscope.

echOpen has to tackle community, research and medical challenges to get all the community around the same table and create the stethoscope of the future: instead of listening to a heart beating, you actually see its beats!

Today, echOpen rests at the heart of Paris, in the historical Hotel-Dieu, with its 10-person core team as well as a community strong of designers, doctors, engineers, … and backed by several institutional actors in professional training, the hospitals (APHP), education (ENS, TelecomParis, …), electronics, and industry (we won for exemple a mentoring with Thales) .We are financially backed by philantropy and prizes we won. 

Here, we developed a [first prototype](http://echopen.org/index.php?title=Category:Emile) as a proof-of-concept, and we are eager to move forward with an integrated device usable for the first clinical tests.

## A bit more context
### The board
The board in itself is not a medical device. The board is a dev kit for the analog part that one could find in any ultrasound probe. It respects the functions and blocks one can find in basically any probe (pulser, TGC, ADC, ..). A main difference is that this board is designed for a single element, and provides so far only a minimal support for the mechanics behind image formation.

Having a single element allows for more space, less density, and to go straight to a regular, though relatively high-speed ADC.

### The Process
None of us had already done an electronic product, so the process in not that of an experienced team, and we're learning on all the fields: writing down an idea, analysing it, structuring it, develop the plans, build it, test it, build the software.. Rince and repeat.

The most challenging part, and somewhere the easiest, will be to allow anyone with little or no experience to replicate our efforts, and to build another copy of the board. Why is that so? With fresh eyes, that's easier to understand what the blocking points could be, what needs to be detailed, and how.

### Debug Sessions

#### Finding the short
The [notes are here](murgen-1.0-short-issue.md) (the murgen-1.0-short-issue.md file). We found the bug, two main issues are to be corrected on board v1.1:
* A short on the ADL5511
* The RECOM has to be mounted upside down, as the pin layout were inverted during the design stage

#### Playing with the board

The notes are here, stemming from the work sessions with the board:

- [Session 1](Session_1.md) : Powering the board, power use, first (bad) trigging and echoes (06 March 2016)
- [Session 2](Session_2.md) : Non-controlled pulsing, inverters, better echoes (11 March 2016)
- [Session 3](Session_3.md) : Getting controlled pulsing, but width not controlled (15 March 2016)
- [Session 4](Session_4.md) : Width of the pulses is getting controlled =) (19 March 2016)
- [Session 4b](Session_4b.md) : Simple data visualisation with BitScope (19 March 2016)
- [Session 5](Session_5.md) : moving the transducer to get the first image ! (20 March 2016)

## Preliminary questions
### Why are we making this?
Because it’s fun, it the first step towards medical open hardware based on ultrasounds, so it’s an element for echOpen !
And because existing hardware doesn’t come in for low-cost, rough uses.
### Who is this for?
This element, comprised of the analog part of ultrasound imaging processing, is aiming hackers, makers, … all who can have fun prototyping a low-cost ultrasound device.
### How will this be used?
This shall be used in conjunction with the mechanical unit (motor, encoder, transducer), and plugged into a small processing unit (aka Raspberry, or BeagleBOne Black for exemple)
### What features does it need to have (now)?
Be able to emit a ultrasound pulse at high voltage, and receive a signal, clean it, detect the envelop and ADC it.
### What features does it need to have (later)?
Shifting envelope detection to software once we’re sure the processing works at “low” rates.
### What are the legacy requirements?
Nothing yet, except a couple of constraints on the use of the tool.
### Who’s going to build this?
Makers, doers, academics, … can use this. But we’d be happy to go with a PCB assembler at first!
### How many do we want to make?
At first, a couple, to prototype it. Once prototyped, this board could be in the hundreds.
### What is the timeline?
BBB investigation had started in September 2015, but following a meetup at echopen’s HQ in Paris end of November, it had been activated again.
**The objective is to get a first functional prototype by February 2015.**
### What are the Goblin and Tobo stuff ?
Those are two alternatives to murgen, in the sense that components may not be the same for goblin, and that tobo is a mini-murgen, limited to the pulser. Goblin is a simpler version, a two-layer one, but we'll need funds to test this one out =)

## Requirements to build the board

### BOM

In the BOM folder !

### At the fab

#### PCB 

A 4-layer PCB.. not so cheap, but at the same time..

#### Fab

Lots around... choose what you want =)

#### Links

PCB Makers
- seeedstudio.com
- PCBshopper.com
PCBA abroad :
- myropcb
- nortechsys
- SeeedStudio only north america
PCBA in france:
- Quad Ind
- PCB-Pool
- EdgeFlex

### Costs

With the french fab we're working with, costs sum to 160e, and they are split as follows, prices being without taxes:
- PCB : 7.34e (but there are overcosts to produce the masks, ...)
- Components : 143.5e and T1-6T-KK81+ (sold by 10): 9.34 each, but can come down to 140e with some volume.
In this case, assembly is close to 120e.

## Technically
### Principles of echography
Basically, echography means plotting echoes. It means we have to create a sound pulse (2), use a good sensor (2), find a way to transform a 1D signal to a 2D image (3), listen to the echoes coming back, cleaning them and  processing them to create an image the way a bat would do (4), and to transmit them to a display (5). 5 steps.
The present project aims at taking care of (1), (4) and (5) - meaning amm electronics related to the analogic part of the imaging.

### System Block Diagram

A full block diagram - Murgen will focus on B-mode imaging

### Narrative of the flow
Since we're using a single sensor (not an array of sensor, as those are used in "regular" machines), we don't have the Beamforming parts. The sensor is similar to a speaker, in the sense that it can be used to generate an acoustic signal from electricity, and vice versa. The flow is therefore as follows:
- A pulse generator generates a high negative voltage pulse, which is as low as possible and to excite the transducer (or crystal), which will resonate at his central frequency. In our case, this is 3.5MHz, but that depends on the transducer being used.
- A signal will come back through the echoes, the reverberation of the acoustic waves on "obstacles", exciting the transducer, having it generate an electric signal.
- This will be prepared by a switch. Indeed, the signal needs to be separated from the excitation. Excitation being at -150V, the signal coming back will be in mV - and it needs to be isolated.
- The signal usually goes through a LNA - low noise amplifier - to be amplified
- then it's processed by a TGC to compensate for signal attenuation. Indeed, the deeper the echoes come back from, the more attenuated they are, and this needs to be corrected.
- An AAF (Anti-Alias Filte) can be put in between, and in the case of the first Murgen release, we also include an enveloppe detection: indeed, echoes are signals that are coming from a couple of ultrasound periods reflected on interfaces, and what interests us is not (at first) the signal itself, rather the enveloppe of it.
- The "cleaned" signal goes through an ADC to be digitalized
- this is output to buffers, in our case to protect the BBB GPIOs.

### Data rates and key figures

- We're aiming at **128 lines/image** - that may be enough at first 
- at **16 imgs/s**, that's 2048 lines/s
--That's 488us per line (for everything: 
- Let's image no further than 15.77cm deep.. Why? Because :
--(15.77 cm x 2) / (154000 cm/s) = 204.805 us 
--that's 1024 pts at 5MHz
--That's **204.805 us** per line
--That's **283.5 us** of idle time - kept for processing, and whatnots
- Final image is therefore **128*1024 px**
--1024 pts for 15.77cm is 6.49px / mm
--That's also 2.1Msps on average or 24Mbit/s.. borderline for data transfer on certain systems.

## Discussions

The bottleneck may lie in the data transfers...

### Data rates and Data bus

- 151202: QuadSPI through a dedicated microcontroleur?
- 151201: At 5Msps, 12 bits, shall we use SPI or parallel? 
- 151201: SPI is managed through hardware... parallel, not. Has to be managed from soft. Can be an issue for real time, and to avoid loosing samples.
- 151130: Rather be going onto SPI : QuadSPI? Is that managed by the RPi? Common amongst ADCs ?
- 151207: For high speed data acquisition: about 120Mbits/sec: No SPI port will support such speed…. Only the  Quad version… we can use USB 2.0 HS for such huge movement.  A FPGA or FPGA/RISC MPU combination can be the best  solution. Later, once on RPI, the data can be handled. But for so  perfect measurement of times, and value, only a DSP it’s not enough.  

### Signal detection

- 151129: LTC5507ES6 to filter ? A rajouter!

### ADC and DAC

- 151130: Better ADC at LTC2315-12
- AD7356 (ual, 12-bit, high speed, low power, successive  approximation ADC that operates from a single 2.5 V power  supply and features throughput rates up to 5 MSPS.  
- DAC: a simple DAC i2c 

### Different setups

- 151202: A DSP may be sufficient for our needs: is that the case? 
- 151203: Proposed setup
 - Using a a Main controller - STM32F407 + USB High speed PHY ?? 
 - Analog frontend :  1/4 of AD8264 as LNA and VGA + AD9236 ADC. TGC  can be controlled by internal STM32 DAC - that's max 100-point TGC  calibration curve.  The ADC then could be connected to DCMI interface of  STM32.
 - Transmitter: could be HV Pulser and the TR switch - microchip HV7360 + MD0100,  STHV 748 
- 151209: In  looking at the issue, I think that DSP can be implemented. Of  course,  that comes with the sourcing and a bit of programming, but it  should  work and provide some flexibility. 
- 151112: 
 - it'd be interesting to keep a 100M s/s sampling rate.  
 - wouldn't recommend MD1210 and TC2320 from supertex for the pulse  part. Those have a recovery time that is quite long, and can get easily  damaged - not to mention that they may be obsolete.  
 - Wouldn't recommend two VGAs ... difficult to control, with a high risk of saturation. 

### 151201 : Electronics for all in one chips: AFE (Analog front end)

#### Rationale 

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

#### Need of a FPGA ?

According to articles and reading, it seems like it will be delicate to proceed without a FPGA for data processing. All "Reference Design" sheets I've read do have a FPGA, or a DSP.... because signals to be processeed are IMHO too fast for a µC.

#### Microcontroler

- Microchip - a µC PIC24FJ128GC010 - ADC, 12 bit, 10 MSPS : http://www.microchip.com/wwwproducts/Devices.aspx?product=PIC24FJ128GC010
- and its dev board at 100$: http://www.microchip.com/Developmenttools/ProductDetails.aspx?PartNO=DM240015
- ST ant its ADC 12 bit 5 MSPS  µC STM32F334R8: http://www.st.com/web/en/catalog/mmc/FM141/SC1169/SS1576/LN1531/PF258875#
- with its dev board at 10 € : http://fr.farnell.com/stmicroelectronics/nucleo-f334r8/carte-dev-32-bits-stm32f334r8/dp/2424210
- Analog Device has a reference list µC  : 
http://www.analog.com/en/products/processors-dsp/analog-microcontrollers/8052-core-products.html
- At analog device, the best seems to be ADSP-CM40XF with a 16 bit ADC at 2,3 MSPS: http://www.analog.com/en/products/processors-dsp/cm4xx-mixed-signal-control-processors/adsp-cm403f.html#product-overview  and its 2 dev boards:
 - http://fr.farnell.com/analog-devices/adzs-cm408f-ezlite/kit-d-eval-ez-kit-lite-adsp-cm408f/dp/2367988?CMP=GRHS-1000059
 - http://fr.farnell.com/analog-devices/adzs-cm403f-ezlite/kit-d-eval-ez-kit-lite-adsp-cm403f/dp/2367987?CMP=GRHS-1000059
- I also found some MCU with an internal ADC and a good rate wich seems interesting : http://www.analog.com/en/products/processors-dsp/analog-microcontrollers/8052-core-products.html and http://www.microchip.com/Developmenttools/ProductDetails.aspx?PartNO=DM240015

### Forks

#### Constraints

- 151124: The tech milestone was on Nov 24th '15 -  and we need to have something by mid Feb' 16.

#### YDO ideas

- 151125: I'm pretty sure that it's impossible that a microcontroler, raspberry or beaglebone can process this data at a speed above 5Msps.  Most of ADCs have a SPI interface, with a 12-bit ADC at 5Msps we'd need a SPI at more than 60Mbps - not everything can do ! In such a case, a DSP or a FPGA is a must-have.

#### LJO/FKA cape

- 151124: let's play with the BBB PRU's and develop a analog+ADC cape.

### HV Supply
HV-supply is going to introduce noise in the circuit.. therefore, a home-made booster was not selected, especially when going at 100V+. We had to options to consider:
- Using a **MAX1711** in [Jatin Sharma thesis](https://www.duo.uio.no/handle/10852/47813), he goes from 12V to 180V. Gerbers and schematics are included in his master).  The board was separated from the rest of the design, to avoid any pickup/noise.
- We have tried the **R05-100B** - a tad more simple, and based on 5V, so easier for us (5V -> 120V).  Schematics are simple, introducing only a couple of capacities.

### Electronics
So far, the key issue is a compromise in terms of data output. It's interesting to see how to interface such data rates to a processing and display unit.

### Setup

#### Jumper 1

This one represents the fixed Gain for the TGC. An extra 18 dB is always handy!

#### Jumper 2
todo
#### ADC Clock:

The 4 options switch allows for a sampling frequency range of choices:

|  R1 |  R2 |  R3 |  R4 | Rset Value | Clock Frequency |
|:---:|:---:|:---:|:---:|:----------:|:---------------:|
|  1  |  2  |  3  |  4  |     Ohm    |      [MHz]      |
| OFF | OFF | OFF | OFF |   Invalid  |     Invalid     |
| OFF | OFF | OFF |  ON |  100000,0  |       1,0       |
| OFF | OFF |  ON | OFF |   40200,0  |       2,5       |
| OFF | OFF |  ON |  ON |   28673,3  |       3,5       |
| OFF |  ON | OFF | OFF |   27400,0  |       3,6       |
| OFF |  ON | OFF |  ON |   21507,1  |       4,6       |
| OFF |  ON |  ON | OFF |   16294,1  |       6,1       |
| OFF |  ON |  ON |  ON |   14011,1  |       7,1       |
|  ON | OFF | OFF | OFF |   20000,0  |       5,0       |
|  ON | OFF | OFF |  ON |   16666,7  |       6,0       |
|  ON | OFF |  ON | OFF |   13355,5  |       7,5       |
|  ON | OFF |  ON |  ON |   11781,9  |       8,5       |
|  ON |  ON | OFF | OFF |   11561,2  |       8,6       |
|  ON |  ON | OFF |  ON |   10363,1  |       9,6       |
|  ON |  ON |  ON | OFF |   8978,9   |       11,1      |
|  ON |  ON |  ON |  ON |   8239,1   |       12,1      |

## Parts, ICs selection (and critical specs)
 
### HV7360:  High Speed, ±100V 2.5A, Two or Three Level Ultrasound Pulser
* High density integration AC coupled pulser
* 0 to ±100V output voltage
* ±2.5A source and sink minimum pulse current
* Up to 35MHz operating frequency
* 2.0ns matched delay times
* 2.5, 3.3 or 5.0V CMOS logic interface
* Low power consumption and very simple to use

HV7360 is a high voltage, high-speed, pulse generator with built-in, fast return to zero damping FETs. This high voltage and high-speed integrated circuit is designed for portable medical ultrasound image devices, but can also can be used for NDT and test equipment applications.

The HV7360 consists of a controller logic interface circuit, level translators, AC coupled MOSFET gate drivers and high voltage and high current P-channel and N-channel MOSFETs as the output stage. The peak output currents of each channel are guaranteed to be over ±2.5A with up to ±100V of pulse swing. The AC coupling topology for the gate drivers not only saves two floating voltage supplies, it also makes the PCB layout easier.
### Protection: MD0100 Datasheet - HV Protection T/R Switch
* Up to ±100V input voltage protection
* Low on resistance - 15O typical
* Fast switching speed
* Effectively, a simple two terminal device
* No external supplies needed

MD0100 is a high voltage, two terminal, bi-directional, current-limiting protection device. The two terminals are interchangeable. It is designed to protect a low noise receiver from the high voltage transmit pulses in ultrasound applications and is commonly referred to as a T/R (transmit and receive) switch. The MD0100 can be considered as a normally closed switch with a typical switching resistance of 15O that allows small signals to pass.

Once the voltage drop across the two terminals exceeds a nominal value of ±2.0V, the device will start to turn off. In the off state, the MD0100 can withstand up to ±100V across its terminals.

A small amount of current, typical of 200µA, is allowed to flow through.
 
### TGC : AD8331 (Single VGA with Ultralow Noise Preamplifier and Programmable RIN)
* Ultralow noise preamplifier
* 3 dB bandwidth: 120 MHz
* Low power: 125 mW/channel
* Wide gain range with programmable postamp (-4.5 dB to +43.5 dB in LO gain mode, 7.5 dB to 55.5 dB in HI gain mode) – we can use this with the corresponding on-board jumper
* Low output-referred noise: 48 nV/vHz typical
* Active input impedance matching
* Optimized for 10-bit/12-bit ADCs : perfect for us
* Selectable output clamping level
* Single 5 V supply operation : ideal for a 5V board supply!

The AD8331 is a single channel, ultralow noise, linear-in-dB, variable gain amplifier (VGA). Optimized for ultrasound systems, it is usable as a low noise variable gain element at frequencies up to 120 MHz.

Included is an ultralow noise preamplifier (LNA), an X-AMP® VGA with 48 dB of gain range, and a selectable gain postamplifier with adjustable output limiting. The LNA gain is 19 dB with a single-ended input and differential outputs. Using a single resistor, the LNA input impedance can be adjusted to match a signal source without compromising noise performance.

The 48 dB gain range of the VGA makes these devices suitable for a variety of applications. Excellent bandwidth uniformity is maintained across the entire range. The gain control interface provides precise linear-in-dB scaling of 50 dB/V for control voltages between 40 mV and 1 V. Factory trim ensures excellent part-to-part and channel-to-channel gain matching. Differential signal paths result in superb second- and third-order distortion performance and low crosstalk.

### TGC  Control : SPI DAC : MAX5383
Controls the TGC
* 8-Bit Resolution in a Miniature 6-Pin SOT23 Package
* Less than 1µA Shutdown Mode
* Low-Glitch Power-On Reset to Zero DAC Output
* 3-Wire SPI/QSPI/MICROWIRE-Compatible Interface : perfect for a SPI interface
* Low 230µA (max) Supply Current

The MAX5383 low-cost, 8-bit digital-to-analog converters (DACs) in miniature 6-pin SOT23 packages have a simple 3-wire, SPI™/QSPI™/MICROWIRE™-compatible serial interface that operates up to 10MHz. The MAX5383 has an internal +2V reference and operates from a +2.7V to +3.6V supply.

The MAX5383 require an extremely low supply current of only 150µA (typ) and provide a buffered voltage output. These devices power up at zero code and remain there until a new code is written to the DAC registers. This provides additional safety for applications that drive valves or other transducers that need to be off on power-up. The MAX5383 include a 1µA, low-power shutdown mode that features software-selectable output loads of 1kO, 100kO, or 1MO to ground.

### Analog envelop detection: ADL5511 - DC to 6 GHz ENVELOPE AND TruPwr™ RMS Detector
* Envelope tracking RF detector with output proportional to input voltage
* No balun or external tuning required
* Input power dynamic range of 47 dB
* Input frequency range from dc to 6 GHz
* 130 MHz envelope bandwidth
* Envelope delay: 2 ns
* Single-supply operation: 4.75 V to 5.25 V

The ADL5511 is an RF envelope and TruPwr™ rms detector. The envelope output voltage is presented as a voltage that is proportional to the envelope of the input signal. The rms output voltage is independent of the peak-to-average ratio of the input signal.
The rms output is a linear-in-V/V voltage with a conversion gain of 1.9 V/V rms at 900 MHz. The envelope output has a conversion gain of 1.46 V/V at 900 MHz and is referenced to an internal 1.1 V reference voltage, which is available on the EREF pin.
The ADL5511 can operate from dc to 6 GHz on signals with envelope bandwidths up to 130 MHz.

### ADC : AD9220 - Complete 12-Bit, 10.0 MSPS Monolithic A/D Converter
* Monolithic 12-Bit A/D Converter Product Family
* Flexible Sampling Rates: 1.5 MSPS, 3.0 MSPS, and 10 MSPS
* Single +5 V Supply
* Out-of-Range Indicator
* 28-SOIC and 28-SSOP

The AD9221/AD9223/AD9220 combine a low cost, high speed single-CMOS process and a novel architecture to achieve the resolution and speed of existing hybrid and monolithic implementations at a fraction of the power consumption and cost. Each device is a complete, monolithic ADC with an on-chip, high performance, low noise sample-and-hold amplifier and programmable voltage reference. An external reference can also be chosen to suit the dc accuracy and temperature drift requirements of the application. The devices use a multistage differential pipelined architecture with digital output error correction logic to provide 12-bit accuracy at the specified data rates and to guarantee no missing codes over the full operating temperature range.

The input of the AD9221/AD9223/AD9220 is highly flexible, allowing for easy interfacing to imaging, communications, medical, and data-acquisition systems. A truly differential input structure allows for both single-ended and differential input sample-interfaces of varying input spans. The sample-and-hold (SHA) amplifier is equally suited for both multiplexed systems that switch full-scale voltage levels in successive channels as well as sampling single-channel inputs at frequencies up to and beyond the Nyquist rate. Also, the AD9221/AD9223/AD9220 is well suited for communication systems employing IF Down Conversion since the SHA in the differential input mode can achieve excellent dynamic performance far beyond its specified Nyquist frequency2.

A single clock input is used to control all internal conversion The digital output data is presented in straight binary format. An out-of-range (OTR) signal indicates an flow condition which can be used with the most significant bit to determine low or high overflow.
 
### Buffers: 74AC541MTC
* Signal isolation is of high value for measurements at this precision (12bit)

The 74AC541 and 74ACT541 are octal buffer/line drivers designed to be employed as memory and address drivers, clock drivers and bus oriented transmitter/ receivers.
 
# Using the Murgen board
## Software / Firmware Summary

Up to v1.0, we're still playing with the board, so there's not interface with the BBB.

However, there's a series of tools to play with the board, one of which being the bitscope, a bit more handy than the redpitaya that the main echopen  project uses, and though it is less precise, we do have less issues (trigging, memory, ...) with it.

## Typical Application

Playing with a broken transducer in a haribo sweet box to see if you can hack ultrasounds.

## User’s Quick-Start Guide
- Install 
--BitScope BitLib
--python math tools
--something to code arduino
- Clone this repo

You're good to go !

# Others
## Discussions 
* Pending work - or refer to the [Discussions.md](Discussions.md) file.
* Check out [the wiki notes](http://echopen.org/index.php?title=Worklog_-_Digging_in_the_shield_option) -- for on-wiki notes of discussions - a tad dirtier.

## Goodies 
Check out [Tobo](tobo/) -- an stand-alone pulser/receiver board and [Goblin](goblin/) for an alternative version.

## People ! 
### Acknowledgement
* Thanks to echOpen =)
* Thanks to Jerome, Farad, Vincent obviously
* Murgen, Sofian, Amit, Emmanuel, Florent, Bertrand & PHH, Mike in a way, list goes on !

# License

Licensed under TAPR Open Hardware License (www.tapr.org/OHL)

Copyright Murgen and Kelu124 (murgen@echopen.org , luc@echopen.org / kelu124@gmail.com ) 2015-2016

# Bibliography

## FPGA-related bibliography
- Structuring a whole ultrasound system on a board: an excellent thesis from P. Levesques (Kyvox),  File:2011 PhilippeLevesque.pdf. 
- A first corresponding article: File:Real-Time Hand-Held Ultrasound Medical-Imaging Device Based on a New Digital Quadrature Demodulation Processor.pdf
- the second corresponding article: File:Novel Low-Power Ultrasound Digital Preprocessing Architecture for Wireless Display.pdf
- Hardware-Software Partitioning of Digital Signal Processing in Ultrasound Medical Devices a Case Study : File:Hardware-Software Partitioning of US probes.pdf
 - File:A Single FPGA-Based Portable Ultrasound Imaging System for Point-of-Care Applications.pdf
 - File:Low-Cost, High-Speed Back-End Processing System for High-Frequency Ultrasound B-Mode Imaging.pdf
- Extremely interesting too,  iPHONE ULTRASOUND By Jonathan Adam, Adam Keen, Dean Santarinala  and File:project2_presentation.pdf their presentation
## Key general articles (base of inspiration for our dear Emile)
- A single monoelement, low-cost ophtalmic probe using a piezo motor : File:Carotenuto ophtalmic prob.pdf : an excellent article. 
- A single monoelement, low-cost USB probe using a CPLD + microcontroller File:Richard low cost probe.pdf, including a great diagram block of the USB probe 
- Saijo USB work : Development of an ultra-portable echo device connected to USB port : Resource: File:2004 Development of an ultra-portable echo device connected to USB port.pdf
- A Software-Based Ultrasound System for Medical Diagnosis by Samir Ram Thadani File:1997 These MIT Thadani.pdf : an excellent introduction the overall design of a US probe design dating back from 1997. 
- Data processing and transfer in echography : File:Design of an Open-Architecture Ultrasound Acquisition System for Real-Time Processing and Control.pdf
- Transducer parameters: File:A focussed transducer-scatterer model for ultrasonic reference st.pdf

## Other

- Projet étudiant, réalisation d'un échographe de poche pour Iphone (très intéressant et très instructif...) : https://courses.engr.illinois.edu/ece445/getfile.asp?id=5167
- White paper de Xilinx : portable ultrasound system : http://www.xilinx.com/support/documentation/white_papers/wp378-Xilinx-in-Portable-Ultrasound.pdf
- Quelques Notes d'applications intéressantes de chez Maxim's :
https://www.maximintegrated.com/en/app-notes/index.mvp/id/5765
 https://www.maximintegrated.com/en/app-notes/index.mvp/id/5553
- Note d'application de chez ST sur "Ultrasound Imaging" :
 - http://www.st.com/web/en/catalog/apps/SE410/AS430/AC404
 - http://www.st.com/web/en/catalog/apps/SE410/AS430/AC404#
- Pulser TI avec Applcation Note d'une solution complète avec des composants TI :
 - http://www.ti.com.cn/cn/lit/ds/symlink/lm96550.pdf

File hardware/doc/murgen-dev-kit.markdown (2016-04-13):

ModuleName: CMP-murgen  

# Module

* CMP-murgen

## Name

murgen-dev-kit

## Description

Getting a home-made open-source ultrasound machine (dev-kit) up and running in your garage / hackerspace / fablab for less than 500$ for the beaglebone black. 

## Narrative

This project is born from a fork from the echOpen project (which aims at providing a low cost, open source ultrasound tool for doctors), with a specific target of providing a technological kit to allow scientists, academics, hackers, makers or OSH fans to hack their way to ultrasound imaging.

# Function: 

The murgen dev-kit sti

# Solutions

(list of solutions, by cliquing it open the corresponding page or dropdown list)

## Constraints 
(contraintes de type commande logique ou alimentation du module)

## Pros

* Dense electronic board
* Use of ICs for all non-trivial functions
* Limited costs (130€ of components + PCB)
* Theoritically compatible with the BeagleBone Black.

## Cons

* Debug is taking time
* PRUs software not yet 

# Interfaces

## Input

* 5V from the CMP-murgen-alim
* 3.3V from the CMP-murgen-alim
* Interfacing with a Trinket Pro: CMP-murgen-trinket
* Transducer: CMP-murgen-transducer

## Output

* Transducer: CMP-murgen-transducer
* Servomotor: CMP-murgen-servo
* Analog outputs on the different TestPoints: CMP-murgen-bitscope

# Versioning

* Version: V1.0
* Date: 19/02/2016
* Technology: Assembling ICs
* Language: python, for the signal processing
* Contributor: Kelu, Murgen, Sofian

# ToDos

* PRUs software

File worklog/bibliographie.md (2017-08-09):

# Our setup

For details, read the bibliography below =)

## Recap and history

|Partie |                                                                                                                              Solutions considérées                                                                                                                            |                 Solutions Choisies                |                    Evolutions considérées?           |
|:---------------------:|:-------------------------------------------------------------------------------------------------------------------------------------------------------------------------------------------------------------------------------------------------------------------------:|:------------------------------------------------------:|:------------------------------:|
|       Transducer      | FURUNO 520-5PSD (Shatin Sharma Thesis) GP2000 (Philippe Levesque) DGH6000 (iPhone Thesis)                                                                                                                                                                                    |                        Recycled                        |             100€ SM            |
|           HV          | HV2901  (10.1109/ULTSYM.2015.0517) MAX1771 (Shatin Sharma Thesis)                                                                                                                                                                                                           |                        R05-100B                        |            R05-100B            |
|       Beamformer      | LM96570  (doi:10.3390/jimaging1010193)                                                                                                                                                                                                                                     |                       Pas besoin                       |           Pas besoin           |
|         Pulser        | MAX14808  (10.1109/ULTSYM.2015.0517) MD1213 mosfet driver + TC6320  (Shatin Sharma Thesis) MD1210 + TC2320 (Philippe Levesque - he doesn't recommend) MAX14808  (10.1109/ULTSYM.2014.0399)  MAX4940 over LM96550 (iPhone Thesis) HV7360 (Recommended)                           |                         HV7360                         |               ???              |
|       Protection      | MD0100 (Shatin Sharma Thesis) TX810 (iPhone Thesis)                                                                                                                                                                                                                         |                         MD0100                         |            MD0105 ?            |
|          TGC          | AFE 5808 IC  (doi:10.3390/jimaging1010193) AD9272 (doi:10.1016/j.jestch.2016.01.008) AFE5S0S (10.1109/ULTSYM.2015.0517) LM96511 (iPhone Thesis) AFE5801 (iPhone Thesis) AD605 (Shatin Sharma Thesis) AD8332 (Philippe Levesque)                                                  | AD8331  controlled over Analog Gain or SPI DAC MAX5383 |             AD8331             |
|  Enveloppe detection  | RC (echOpen)                                                                                                                                                                                                                                                               |                         ADL5511                        |       A tester en modules      |
|          ADC          | LTC2245  (Shatin Sharma Thesis) AFE5808 (10.1109/ULTSYM.2014.0399) ADC10040 (Philippe Levesque) AD9236  (Recommended) STM32F334R8 (Recommended, 12bits, 5Msps)                                                                                                                 |              AD9220 + Buffer (74AC541MTC)               | LTC2314-14 pour son aspect SPI |
|   Signal Processing   | Xilinx Kintex-7 FPGA (doi:10.3390/jimaging1010193) Xilinx FPGAs (doi:10.1016/j.jestch.2016.01.008) Spartan6, Xilinx (10.1109/ULTSYM.2015.0517) Spartan 6 LX150 (10.1109/ULTSYM.2014.0399) XC3S1500L-FG320, FPGA Xilinx  (Philippe Levesque) Altera Cyclone III (iPhone Thesis)  |                        BitScope                        |                                |
|        Display        | Raspberry Pi 2 (doi:10.3390/jimaging1010193)                                                                                                                                                                                                                               |                     Linux Computer                     |                                |
|          Cout         | NA                                                                                                                                                                                                                                                                        |                          470 €                         |              250 €             |

## Parts, ICs selection (and critical specs)
 
### HV7360:  High Speed, ±100V 2.5A, Two or Three Level Ultrasound Pulser
* High density integration AC coupled pulser
* 0 to ±100V output voltage
* ±2.5A source and sink minimum pulse current
* Up to 35MHz operating frequency
* 2.0ns matched delay times
* 2.5, 3.3 or 5.0V CMOS logic interface
* Low power consumption and very simple to use

HV7360 is a high voltage, high-speed, pulse generator with built-in, fast return to zero damping FETs. This high voltage and high-speed integrated circuit is designed for portable medical ultrasound image devices, but can also can be used for NDT and test equipment applications.

The HV7360 consists of a controller logic interface circuit, level translators, AC coupled MOSFET gate drivers and high voltage and high current P-channel and N-channel MOSFETs as the output stage. The peak output currents of each channel are guaranteed to be over ±2.5A with up to ±100V of pulse swing. The AC coupling topology for the gate drivers not only saves two floating voltage supplies, it also makes the PCB layout easier.
### Protection: MD0100 Datasheet - HV Protection T/R Switch
* Up to ±100V input voltage protection
* Low on resistance - 15O typical
* Fast switching speed
* Effectively, a simple two terminal device
* No external supplies needed

MD0100 is a high voltage, two terminal, bi-directional, current-limiting protection device. The two terminals are interchangeable. It is designed to protect a low noise receiver from the high voltage transmit pulses in ultrasound applications and is commonly referred to as a T/R (transmit and receive) switch. The MD0100 can be considered as a normally closed switch with a typical switching resistance of 15O that allows small signals to pass.

Once the voltage drop across the two terminals exceeds a nominal value of ±2.0V, the device will start to turn off. In the off state, the MD0100 can withstand up to ±100V across its terminals.

A small amount of current, typical of 200µA, is allowed to flow through.
 
### TGC : AD8331 (Single VGA with Ultralow Noise Preamplifier and Programmable RIN)
* Ultralow noise preamplifier
* 3 dB bandwidth: 120 MHz
* Low power: 125 mW/channel
* Wide gain range with programmable postamp (-4.5 dB to +43.5 dB in LO gain mode, 7.5 dB to 55.5 dB in HI gain mode) – we can use this with the corresponding on-board jumper
* Low output-referred noise: 48 nV/vHz typical
* Active input impedance matching
* Optimized for 10-bit/12-bit ADCs : perfect for us
* Selectable output clamping level
* Single 5 V supply operation : ideal for a 5V board supply!

The AD8331 is a single channel, ultralow noise, linear-in-dB, variable gain amplifier (VGA). Optimized for ultrasound systems, it is usable as a low noise variable gain element at frequencies up to 120 MHz.

Included is an ultralow noise preamplifier (LNA), an X-AMP® VGA with 48 dB of gain range, and a selectable gain postamplifier with adjustable output limiting. The LNA gain is 19 dB with a single-ended input and differential outputs. Using a single resistor, the LNA input impedance can be adjusted to match a signal source without compromising noise performance.

The 48 dB gain range of the VGA makes these devices suitable for a variety of applications. Excellent bandwidth uniformity is maintained across the entire range. The gain control interface provides precise linear-in-dB scaling of 50 dB/V for control voltages between 40 mV and 1 V. Factory trim ensures excellent part-to-part and channel-to-channel gain matching. Differential signal paths result in superb second- and third-order distortion performance and low crosstalk.

### TGC  Control : SPI DAC : MAX5383
Controls the TGC
* 8-Bit Resolution in a Miniature 6-Pin SOT23 Package
* Less than 1µA Shutdown Mode
* Low-Glitch Power-On Reset to Zero DAC Output
* 3-Wire SPI/QSPI/MICROWIRE-Compatible Interface : perfect for a SPI interface
* Low 230µA (max) Supply Current

The MAX5383 low-cost, 8-bit digital-to-analog converters (DACs) in miniature 6-pin SOT23 packages have a simple 3-wire, SPI™/QSPI™/MICROWIRE™-compatible serial interface that operates up to 10MHz. The MAX5383 has an internal +2V reference and operates from a +2.7V to +3.6V supply.

The MAX5383 require an extremely low supply current of only 150µA (typ) and provide a buffered voltage output. These devices power up at zero code and remain there until a new code is written to the DAC registers. This provides additional safety for applications that drive valves or other transducers that need to be off on power-up. The MAX5383 include a 1µA, low-power shutdown mode that features software-selectable output loads of 1kO, 100kO, or 1MO to ground.

### Analog envelop detection: ADL5511 - DC to 6 GHz ENVELOPE AND TruPwr™ RMS Detector
* Envelope tracking RF detector with output proportional to input voltage
* No balun or external tuning required
* Input power dynamic range of 47 dB
* Input frequency range from dc to 6 GHz
* 130 MHz envelope bandwidth
* Envelope delay: 2 ns
* Single-supply operation: 4.75 V to 5.25 V

The ADL5511 is an RF envelope and TruPwr™ rms detector. The envelope output voltage is presented as a voltage that is proportional to the envelope of the input signal. The rms output voltage is independent of the peak-to-average ratio of the input signal.
The rms output is a linear-in-V/V voltage with a conversion gain of 1.9 V/V rms at 900 MHz. The envelope output has a conversion gain of 1.46 V/V at 900 MHz and is referenced to an internal 1.1 V reference voltage, which is available on the EREF pin.
The ADL5511 can operate from dc to 6 GHz on signals with envelope bandwidths up to 130 MHz.

### ADC : AD9220 - Complete 12-Bit, 10.0 MSPS Monolithic A/D Converter
* Monolithic 12-Bit A/D Converter Product Family
* Flexible Sampling Rates: 1.5 MSPS, 3.0 MSPS, and 10 MSPS
* Single +5 V Supply
* Out-of-Range Indicator
* 28-SOIC and 28-SSOP

The AD9221/AD9223/AD9220 combine a low cost, high speed single-CMOS process and a novel architecture to achieve the resolution and speed of existing hybrid and monolithic implementations at a fraction of the power consumption and cost. Each device is a complete, monolithic ADC with an on-chip, high performance, low noise sample-and-hold amplifier and programmable voltage reference. An external reference can also be chosen to suit the dc accuracy and temperature drift requirements of the application. The devices use a multistage differential pipelined architecture with digital output error correction logic to provide 12-bit accuracy at the specified data rates and to guarantee no missing codes over the full operating temperature range.

The input of the AD9221/AD9223/AD9220 is highly flexible, allowing for easy interfacing to imaging, communications, medical, and data-acquisition systems. A truly differential input structure allows for both single-ended and differential input sample-interfaces of varying input spans. The sample-and-hold (SHA) amplifier is equally suited for both multiplexed systems that switch full-scale voltage levels in successive channels as well as sampling single-channel inputs at frequencies up to and beyond the Nyquist rate. Also, the AD9221/AD9223/AD9220 is well suited for communication systems employing IF Down Conversion since the SHA in the differential input mode can achieve excellent dynamic performance far beyond its specified Nyquist frequency2.

A single clock input is used to control all internal conversion The digital output data is presented in straight binary format. An out-of-range (OTR) signal indicates an flow condition which can be used with the most significant bit to determine low or high overflow.
 
### Buffers: 74AC541MTC
* Signal isolation is of high value for measurements at this precision (12bit)

The 74AC541 and 74ACT541 are octal buffer/line drivers designed to be employed as memory and address drivers, clock drivers and bus oriented transmitter/ receivers.

# Inspiration from other articles

##  FPGA-Based Portable Ultrasound Scanning System with Automatic Kidney Detection

### Article information
* **Keywords:** learning, fpga, raspberry
* **Uses:** Automatic kidney detection
* **Who:** raji@iith.ac.in (x)
* **Date:** 04/12/2015
* **DOI:** : doi:10.3390/jimaging1010193

### Overall information
*  **Notes:** Awesome work for image segmentation using a Raspberry Pi 2.
*  **Image data**: 22 fps at 480 x 640

### Electronics
* **HV**:  
* **Pulser**:  
* **Beamformer**: LM96570
* **Transducer**:  64-element
* **Protection**:  
* **TGC**:  AFE 5808 IC
* **ADC**:  14bit, 40 MHz
* **DAC**:  
* **Processing**:   Xilinx Kintex-7 FPGA
* **Transfer**:  RS-232 
* **Image processing**:  Raspberry Pi ARM

##  Low Complex, Programmable FPGA based 8-Channel Ultrasound Transmitter for Medical Imaging Researches

### Article information
* **Keywords:**  FPGA, AFE,
* **Uses:**  Prototype
* **Who:**  ee12m1014, raji, sureshpulig@iith.ac.in (x)
* **Date:**  2014
* **DOI:** :  978-1-4799-6644-8/14/$31.00 ©2014 IEEE

### Overall information
*  **Notes:**
*  **Image data**:

### Electronics
* **HV**:  
* **Pulser**:  
* **Beamformer**: LM96570 (single high speed 4-wire serial interface for transmission parameters)
* **Transducer**:  
* **Protection**:  
* **TGC**:  AFE 5809
* **ADC**:  
* **DAC**:  
* **Processing**:  Spartan 3E FPGA
* **Transfer**:  
* **Image processing**:  A Graphical User Interface (GUI) has been developed with National Instruments LabVIEW 2012 in the Microsoft Windows platform. Spartan

##  Microcontroller USB interfacing with MATLAB GUI for low cost medical ultrasound scanners

### Article information
* **Keywords:** microcontroller, matlab
* **Uses:** academics, research 
* **Who:** Jean Rossario Raj - bmz108120@cbme.iitd.ac.in (x)
* **Date:** Accepted 12 January 2016
* **DOI:** : doi:10.1016/j.jestch.2016.01.008

### Overall information
*  **Notes:** This is an open access article under the CC BY-NC-ND license
*  **Image data**:

### Electronics
* **HV**:  
* **Pulser**:  
* **Beamformer**:  
* **Transducer**:  
* **Protection**:  
* **TGC**:  AD9272
* **ADC**:  
* **DAC**:  
* **Processing**:  Xilinx FPGAs
* **Transfer**:  C8051F340
* **Image processing**:  

## Smartphone-based Portable Ultrasound Imaging System : A Primary Result 

### Article information
* **Keywords:**   
* **Uses:**  
* **Who:**    Kyu Cheol Kim
* **Date:**  2013
* **DOI:**   10.1109/ULTSYM.2013.0526

### Overall information
*  **Notes:** Nothing was electronics, all smartphone.  The ultrasound B-mode image reconstructed from the Android smartphone where an 850×800 image is reconstructed and displayed. The total execution time to perform core functional blocks for 128-scanline, 512-sample data is about 520 milliseconds. 
*  **Image data**:   128x512

### Electronics
* **HV**:  
* **Pulser**:  
* **Beamformer**:  
* **Transducer**:   V10, Samsung Medison, Seoul, Korea
* **Protection**:  
* **TGC**:  
* **ADC**:  
* **DAC**:  
* **Processing**:  
* **Transfer**:   
* **Image processing**:  GPU in Samsung’s Galaxy Note II smartphone

##  Smartphone-based  Portable  Ultrasound  Imaging    System: Prototype Implementation and Evaluation 

### Article information
* **Keywords:** smartphone, hardware, software
* **Uses:** Smartphone
* **Who:** Sewoong Ahn
* **Date:** 2015
* **DOI:** : 10.1109/ULTSYM.2015.0517

### Overall information
*  **Notes:** : probe de 180 x 55 x 35mm, 180g
*  **Image data**: 58 fps

### Electronics
* **HV**:  HV2901 (70V-peak voltage)
* **Pulser**:  MAX14808 two 8-channel pulsers
* **Beamformer**: 
* **Transducer**:  128element transducer 16-channel probe system
* **Protection**:  
* **TGC**:  two 8-channel analog front-end chip (AFE5S0S, Texas Instruments, TX, USA) which include low noise amplifiers (LNA) and analog-to-digital converters (ADC).
* **ADC**:  40MHz
* **DAC**:  
* **Processing**:   Spartan6, Xilinx Inc.
* **Transfer**:  USB30l4-BZX -- USB 3.0
* **Image processing**:  Galaxy S5 LTE-A, Samsung., Korea

##  PC-Based Modular Digital US Imaging System

### Article information
* **Keywords:**  
* **Uses:**  
* **Who:** Amr M. Hendy - ahendy@ibetech.com
* **Date:**  
* **DOI:**  

### Overall information
*  **Notes:** Working mostly with Hilbert transforms
*  **Image data**:

### Electronics
* **HV**:  
* **Pulser**:  
* **Beamformer**: LM96570
* **Transducer**:  
* **Protection**:   
* **TGC**:   
* **ADC**:  
* **DAC**:  
* **Processing**:  Virtex-5 FPGA
* **Transfer**:   8-lane PCIe interface	
* **Image processing**:  Pentium 3.0 GHz Core 2 Quad PC with 8 GB memory

## Development of a wide band front end echo sounder receiver circuit

### Article information
* **Keywords:**   
* **Uses:**  Maritime
* **Who:**   Jatin Sharma
* **Date:**   August 2015
* **DOI:**  Department of Physics, University of Oslo

### Overall information
*  **Notes:**
*  **Image data**:  

### Electronics
* **HV**:  MAX1771 
* **Pulser**:  MD1213 mosfet driver (The other similar options were MD1210 and MD1211. But MD1213 was the preferred choice because Bipolar output voltage of 5V can also be achieved with this chip if desired.) + TC6320 mosfet pair
* **Beamformer**:  
* **Transducer**:  FURUNO 520-5PSD  (200kHz) 
* **Protection**:  MD0100. Switch MD0101 is also a good option as it has integrated clamp diodes and therefore no need of external diodes but it is useful when there are more number of channels in the system. Similarly, if voltages greater than §100V are used for transmission, then the switchMD0105 can be used. This switch can be used for protection against voltages up to §130V .
* **TGC**:  Amplifier AD605 is used in this project. AD605 is a low noise, differential-input, dual-channel, linear-in-dB Variable Gain Amplifier. It fulfills the desired characteristics of gain, noise, supply voltage etc. It comprises of two variable gain amplifiers which can be connected in series to get higher gain ranges, up to 96dB and it uses a common gain voltage(VGN) for both the amplifiers to control the variable gain.
* **ADC**:  LTC2245 is a 14-bit, 10Msps ADC. It needs a single 3V Supply making it compatible with the rest of the components.
* **DAC**:  
* **Processing**:  
* **Transfer**:   
* **Image processing**:  

##  A New Smart Probe System for a Tablet PC-based Point-of-Care Ultrasound Imaging System Feasibility Study

### Article information
* **Keywords:**  POCUS, feasibility, tablet
* **Uses:**  POCUS
* **Who:**  Yeongnam Lee
* **Date:** 
* **DOI:** 10.1109/ULTSYM.2014.0399

### Overall information
*  **Notes:** small probe : 73 g, 150 mm x 40 mm x 10 mm, 7W
*  **Image data**: 22 Hz of frame rate  

### Electronics
* **HV**:  
* **Pulser**:  MAX14808 (two 8-channel pulsers with transmit/receive switch)
* **Beamformer**:  
* **Transducer**:  7.5MHz - 16-channel
* **Protection**:  
* **TGC**:  
* **ADC**:  AFE5808 : two analog-to-digital converters 40 MHz
* **DAC**:  
* **Processing**: Spartan 6 LX150 
* **Transfer**:  USB3
* **Image processing**: ATIV Smart PC, Samsung

##  Very Fast Scanning Probe for Ophthalmic Use

### Article information
* **Keywords:** ophthalmic
* **Uses:** ophthalmic
* **Who:**  Carotenuto - r.carotenuto@ing.unirc.it
* **Date:**  
* **DOI:** 

### Overall information
*  **Notes:**
*  **Image data**: 256 lines at 25fps

### Electronics
* **HV**:  
* **Pulser**:  
* **Beamformer**: by µC : Scenix SX by Parallax,
* **Transducer**:  PVDF, single, 35MHz
* **Protection**:  
* **TGC**:  
* **ADC**:  
* **DAC**:  
* **Processing**:  
* **Transfer**:  Scenix SX by Parallax
* **Image processing**:  

##  ARCHITECTURE D’UN PROCESSEUR DÉDIÉ AUX TRAITEMENTS DE SIGNAUX ULTRASONIQUES EN TEMPS RÉEL 

### Article information
* **Keywords:** FPGA, mecanique
* **Uses:**  Prototype
* **Who:**  Philippe Levesque
* **Date:**  2011
* **DOI:** 

### Overall information
*  **Notes:**
*  **Image data**: 25 fps 320x240 pixels

### Electronics
* **HV**:  
* **Pulser**:  MD1210 et TC2320
* **Beamformer**: 
* **Transducer**: GP2000 5 MHz, Interson 
* **Protection**:  
* **TGC**:  AD8332
* **ADC**:  ADC10040 - 10 bits, 10Msps
* **DAC**:  10 Msps
* **Processing**: XC3S1500L-FG320, Xilinx  
* **Transfer**:  
* **Image processing**:  

##  A Low Cost Open Source High Frame-Rate High-Frequency Imaging System

### Article information
* **Keywords:** bimorph, OpenHiFUS, ohptalmic
* **Uses:**  ophtalmic
* **Who:** J.A. Brown - j.brown@dal.ca
* **Date:** 
* **DOI:**  

### Overall information
*  **Notes:**
*  **Image data**:

### Electronics
* **HV**:  
* **Pulser**:  
* **Beamformer**: 
* **Transducer**: Daxsonics 45MHz + Arduino Nano 
* **Protection**:  
* **TGC**:  
* **ADC**:  500 MHz 12 bit PCIe digitizer
* **DAC**:  
* **Processing**:  Xilinx, Virtex V,
* **Transfer**:  
* **Image processing**:  

##  iPHONE ULTRASOUND

### Article information
* **Keywords:**  iPHONE, jack
* **Uses:**  
* **Who:**  Jonathan Adam, Adam Keen, Dean Santarinala
* **Date:**  
* **DOI:** Final Report for ECE 445, Senior Design, Spring 2012

### Overall information
*  **Notes:** AFE5801 
*  **Image data**:

### Electronics
* **HV**:  
* **Pulser**:  MAX4940 over LM96550. Our original design employed Texas Instrument’s LM96550 ultrasound transmit pulser. After several failed attempts to achieve correct operation, however, we used Maxim IC’s MAX4940 high-voltage digital pulser instead. The MAX4940’s design includes four channels, as well as positive and negative high-voltage supplies up to +220V and -220V, respectively. Since our application is a one-dimensional scan, only one channel was utilized.
* **Beamformer**:  
* **Transducer**:  DGH 6000 Scanmate A transducer (10.0 MHz). It focuses an acoustic beam at 23.0 mm nominal and has a circular patient contact area 0.275” in diameter.
* **Protection**:  TX810 or LM96530
* **TGC**:  AFE5801, LM96511 more complicated. The AFE5801 includes an 8-channel variable-gain amplifier (VGA) and an 8-channel, 12bit, high-speed analog-to-digital converter (ADC) based on a switched capacitor design.
* **ADC**:  
* **DAC**:  
* **Processing**:  Altera Cyclone III. The Altera Cyclone III is a powerful Field-Programmable Gate Array (FPGA) featuring 10,320 Logic Elements. Its 144 pins are divided into three sections below by function, and the communication protocol with the iPhone is discussed.
* **Transfer**:  
* **Image processing**:  iPhone

##  A Low-Cost B-Mode USB Ultrasound Probe

### Article information
* **Keywords:**  mechanical
* **Uses:**  
* **Who:**  WILLIAM D. RICHARD - wdr@zandrtech.com
* **Date:**  
* **DOI:**  

### Overall information
*  **Notes:**
*  **Image data**: 256x512

### Electronics
* **HV**:  
* **Pulser**:  
* **Beamformer**:  
* **Transducer**:   12.5 MHz ophthalmic probe.
* **Protection**:  
* **TGC**:  
* **ADC**:  
* **DAC**:  
* **Processing**:  Complex Programmable Logic Device (CPLD)
* **Transfer**:  CY7C68014A - a com plete USB 2.0 in ter face, 4 KB of Static RAM (SRAM) for buffering high-speed USB data and an 8051 microprocessor with 16 KB of code/data SRAM all integrated into a single chip. This IC runs embedded 8051 code stored in the I2C Bus Serial PROM (SPROM) or that has been down loaded from the host via a process called ‘ReNumeration.’
* **Image processing**:  

Other 
===

### Links

 * [Murgen  on hackaday](http://hackaday.io/project/9281-murgen) for some news
 * [sci-hub.io](http://sci_hub.io/) for syntax highlighting in output code blocks

# Template

## Name of the article

### Article information
* **Keywords:**   
* **Uses:**  
* **Who:**   
* **Date:**  
* **DOI:**  

### Overall information
*  **Notes:**
*  **Image data**:  

### Electronics
* **HV**:  
* **Pulser**:  
* **Beamformer**:  
* **Transducer**:  
* **Protection**:  
* **TGC**:  
* **ADC**:  
* **DAC**:  
* **Processing**:  
* **Transfer**:   
* **Image processing**:

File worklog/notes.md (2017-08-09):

Some work with my
AA813B03480B306D773BFD007800AA5F3D83C176E822C5096CA57632284D8D0E friend
;)

Work
----

### TODO

-   Validate board
-   Do PRU code
-   Do "datadump" code
-   Do Node.js
    -   Explore WebRTC
-   USB connection

### Pending

-   Transducer sourcing

### Done

-   Assembling a small team (24/11/15 -&gt; onwoards)
-   Pre BOM (30/11/15)
-   Prefeasibility study (4/12/15)
-   Finding PCB/PCBA suppliers (7/12/15)
-   BOM
-   Add to the list ADS803E or LTC2315-12
-   A PCB feasibility (Manu, S, A)
-   A PCB pre-design

### Cancelled

-   [Design thinking
    classes](https://www.coursera.org/learn/design-thinking-innovation/home/welcome)

### Thoughts

-   See below \^\^

Culture
-------

-   [Read Meaningful Making
    (PDF eBook)](http://fablearn.stanford.edu/fellows/sites/default/files/Blikstein_Martinez_Pang-Meaningful_Making_book.pdf)
-   [Here from Alessia
    Cara](https://www.youtube.com/watch?v=eyoSkZ-KODE)

Dimensioning the data
---------------------

* 128 lines/image may be enough at first - at 16 imgs/s thats 2048 lines/s
    * That's 488us per line
* (15.77 cm x 2) / (154000 cm/s) = 204.805 us - that's 1024 pts at 5MHz
        * That's 204.805 us per line
        * That's 283.5 us of idle time
* Final image is therefore 128*1024 px
        *  1024 pts for 15.77cm is 6.49px / mm
        * That's 2.1Msps on average

This LOG
--------

### Nov 24th 2015

-   TLDR
    -   CapTech Workshop. Was great!
    -   Acted upon a split between a FPGA long-term approach, and a
        non-FPGA one. I remembered those good old times when this was
        a possibility.
    -   Damn it. What if I could dig into this? Not µC, rather an
        extension for an existing computer.. or mini computer.
    -   Saw some ideas on the Arduino's side. Separate ADC.
-   Resources
    -   [Is Pi powerful enough for an oscilloscope
        project?](http://raspberrypi.stackexchange.com/questions/4129/is-pi-powerful-enough-for-an-oscilloscope-project)
    -   [Raspberry Pi as an Oscilloscope @ 10
        MSPS](https://digibird1.wordpress.com/raspberry-pi-as-an-oscilloscope-10-msps/)

### Nov 27th 2015

-   http://paul.sullivan.za.org/raspberry-pi-oscilloscope/EE-October-1991/
    (pics below)
-   MagPi : ISSUE 24 - JUN 2014 (to print !!)
-   Follow up
    -   Discussion with
        4365D2F5E4EB59B6BAD0FC746506A6EADEC28BC264BDD78BC041D3417B0766F4
    -   Discussion with
        8620B4ADDED83F8C1E5EBC0F401D12BC327735D7A314336D24C3F3D88A16E3ED

### Nov 28th

-   Tamagotchi hive in a probe?
-   Thinking about the smile on the silkscreen. EO+OH+PI+Pirate?

### Dec 1st

* Thinking of deadlines
* PHH/BM discussions

	* Rather be going onto SPI : QuadSPI ?
	* LTC5507ES6 to filter ? A rajouter!
	* Better ADC at LTC2315-12
	* DAC: a simple DAC i2c

echOpen discussion

* Pro/Cons of a shield compared to FPGA/microcontrolleur

### Dec 2nd

-   Rasberry Pirn
    -   Raspberry Pi Zero Headless Setup :
        http://davidmaitland.me/2015/12/raspberry-pi-zero-headless-setup/
    -   Installing Operating System Images on Linux
        https://www.raspberrypi.org/documentation/installation/installing-images/linux.md
-   BBB
    -   How to use it?
        -   http://www.element14.com/community/community/designcenter/single-board-computers/next-gen_beaglebone//blog/2013/05/22/bbb--working-with-the-pru-icssprussv2
        -   For low-speed comms, conventional I2C or similar protocols
            can be used, and there is no need to use a PRU. For
            high-speed comms the PRU may be extremely useful because it
            can service the hardware with no interruptions due to Linux
            context switching, and no overhead is experienced by the
            main ARM processor. Here are some examples that should be
            feasible; basically quite a few possibilities, such as
            **interfacing to a fast ADC (e.g. analog capture)**,
    -   https://theembeddedkitchen.net/beaglelogic-building-a-logic-analyzer-with-the-prus-part-1/449
        BBB is a 100MHz logic analyzer on a BeagleBoneBlack
    -   Demo over the http://beaglelogic.github.io/webapp/
    -   http://r.git.net/beagleboard/2013-10/msg00204.html
        -   Can the PRU be used to interface the Beaglebone to external
            ADC? I need to capture 500 micro-seconds of data at a 5
            MHz rate.
        -   -&gt; *It depends on the interface to the ADC. There is a
            parallel capture interface that will easily run that fast,
            and you may be able to use the bit-shift interface to do
            serial or something like SPI if the PRU's capability lines
            up with what your ADC wants to see.*
    -   http://www.element14.com/community/community/designcenter/single-board-computers/next-gen_beaglebone//blog/2013/08/04/bbb--high-speed-data-acquisition-and-web-based-ui
        -   *In its current state, it grabs analog data from an ADC, and
            dumps it into memory on the BBB, ready to be displayed or
            further processed. It could be used for gathering analog
            information from sensors, CCDs or other data
            acquisition use-cases. To be reasonably useful, the desire
            was for it to support 20Mbytes/sec of data or more. It does
            achieve this, but it is for further study to find higher
            speed methods.*
        -   *This is not such a bad idea, because in future the ADC
            could be swapped out to a (say) 10-bit ADC with no code
            change on the PRU.*
        -   **Once the data has been captured (2000 samples in this
            example), the command byte is acknowledged, so that the
            Linux hosted application can know that the PRU
            has completed. The PRU now sits and waits for a new
            instruction from the Linux hosted application.** -&gt; works
            for us - fixed depth = fixed \# of samples
    -   Buffer to be used : detailed at
        http://www.element14.com/community/community/designcenter/single-board-computers/next-gen_beaglebone//blog/2013/08/04/bbb--high-speed-data-acquisition-and-web-based-ui
        -   ''These were extremely important for two reasons. One reason
            is that the pins to the BBB that I wished to use need to be
            isolated during power-up, because they are used for
            selecting the boot method. If there was any unusual level on
            the pins upon power-up then the BBB will not boot from
            the eMMC. So, a tri-state buffer is needed. The other reason
            is that there is a fair bit of capacitance and it is highly
            likely that the ADC may not be able to directly drive the
            pins at high speed. I actually came across this problem
            while trying to connect a camera to the BBB. I struggled for
            days without realising that the camera could not support
            the load. So, the buffers are likely to be essential for
            most designs using the pins that were selected. I used a
            74LVC244A device as a buffer. Note that the clock also needs
            a buffer, unless significant jitter is acceptable. No
            tri-state is required here, so I used a MC74VHC1GT50.

''

### Dec 3rd
* New ADCs in mind
        ADS803E
        LTC2315-12 
* Orange Pi Plus 2 : A nasty little thing
* BBB as always coming mostly from element14
        Some limits - not exploiting all ? http://exploringbeaglebone.com/chapter13/#The_ADS7883_Single-Channel_12-bit_ADC_1MSps_max
        SPI speed with BBB : http://fr.mathworks.com/help/supportpkg/beagleboneio/ug/use-the-beaglebone-black-spi-interface-to-connect-to-a-device.html (up to 32MHz) - which is
* 16 bits : is it possible to set all 16 pins on pru0 as inputs? I saw you mentioned something about disabling the microSD functionality on the BB to get access to all 16 pins, but I wasn't exactly sure how. -- heartofasquid
        I thought the PRUs had a 16bit parallel capture mode or are all the pins not available on the BBB? (need to consult the docs) section 4.5.2.2.3.2 of the tech ref spruh73c.pdf One thought I had was to use both PRUs to capture alternate bytes/words but that was just a thought, again are all the pins available?
        I'd made a mistake, it looks like all of PRU0's GPI pins may be available, if we are happy to lose the microSD (no big loss - there are other ways to get data in/out of the BBB). So, we can theoretically get high-res captures up to about 15bits, if we need 1 pin for the clock.
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

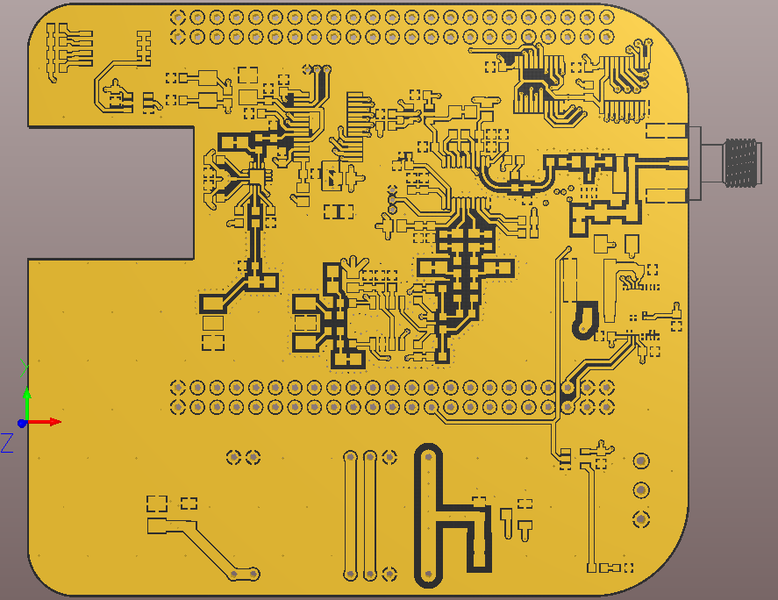
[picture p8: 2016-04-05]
hardware/3D/Top_Copper.png

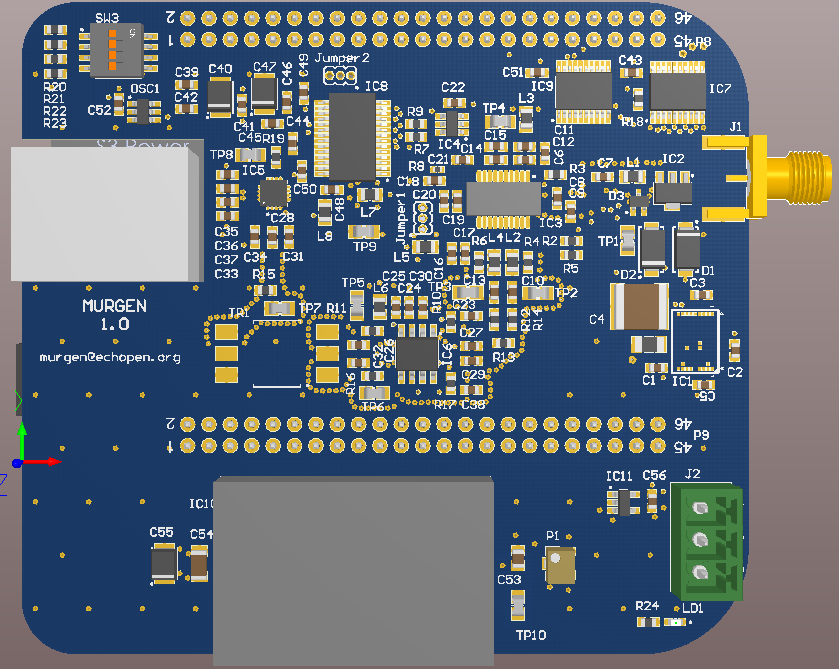
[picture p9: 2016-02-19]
hardware/3D/Murgen Cape 1.0.png

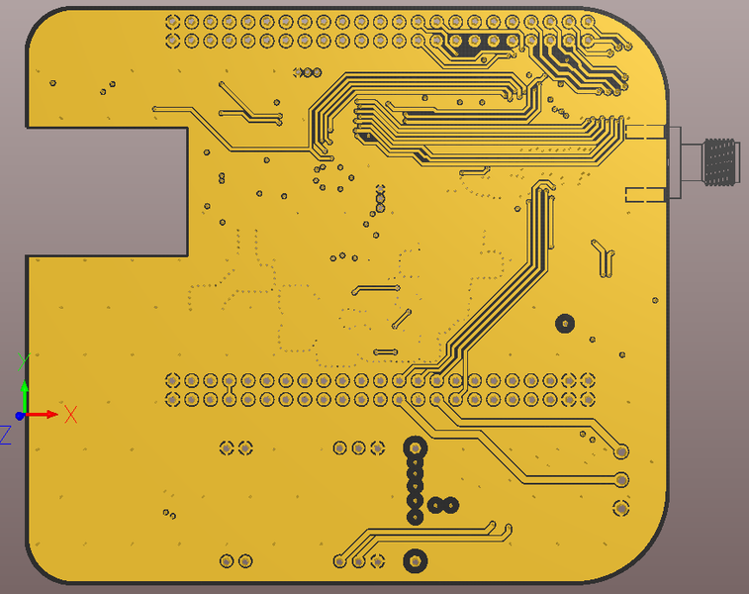
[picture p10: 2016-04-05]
hardware/3D/Bottom_Copper.png

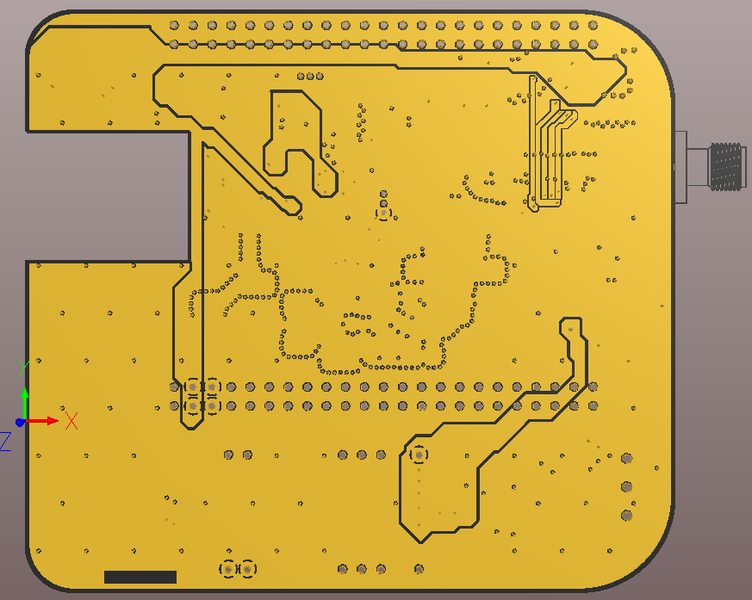
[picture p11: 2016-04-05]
hardware/3D/Power_Plane.png

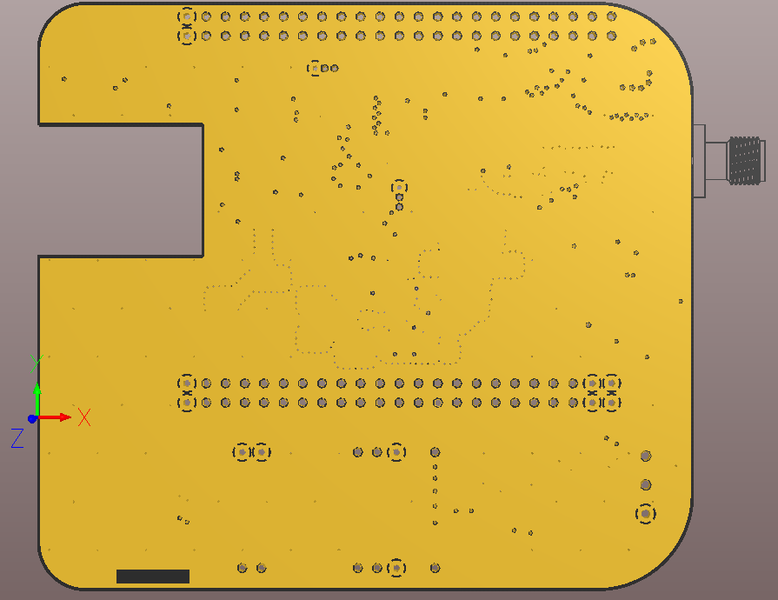
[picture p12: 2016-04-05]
hardware/3D/Ground_Plane.png

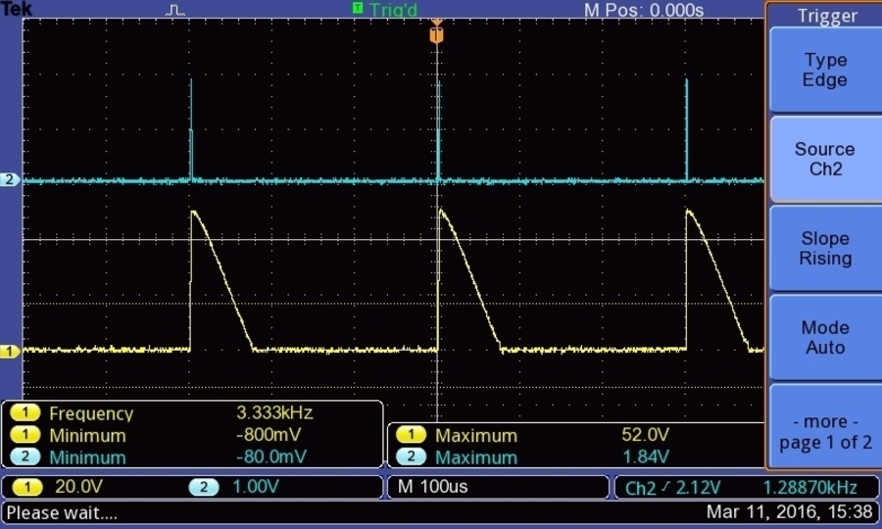
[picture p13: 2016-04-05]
worklog/Images/Session_2/TEK0000.JPG

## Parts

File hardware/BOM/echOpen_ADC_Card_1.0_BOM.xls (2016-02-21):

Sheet: BOM Report
Bill of Materials |  |  | Bill of Materials For PCB Document [echOpen_ADC_Card.PcbDoc]
Source Data From: |  | echOpen_ADC_Card.PcbDoc
Project: |  | echOpen_ADC_Card.PrjPcb
Variant: |  | None
Creation Date: | 1/10/2016 | 11:40:20 PM
Print Date: | 2016-01-10 | 42379.98644
Designator |  |  | Value | Description | Manufacturer Part Number | Manufacturer1 Part Number | Quantity
C1, C2, C3, C5, C6, C7, C10, C11, C13, C14, C15, C17, C18, C19, C22, C25, C26, C28, C30, C32, C36, C39, C41, C42, C43, C45, C46, C48, C49, C50, C51, C52, C56 |  |  | 100nF | Non-polarised capacitor | CC0603_100NF_50V_10%_X7R | 223858615649 | 33
C4 |  |  | 1uF | Non-polarised capacitor | CC2220_1UF_200V_10%_X7R | C2220X105K2RAC | 1
C8 |  |  | 18nF | Non-polarised capacitor | CC0603_18NF_50V_10%_X7R | 223858615639 | 1
C9 |  |  | 22pF | Non-polarised capacitor | CC0603_22PF_50V_5%_NP0 | 223886715229 | 1
C12, C16, C20, C24 |  |  | 1nF | Non-polarised capacitor | CC0603_1NF_50V_10%_X7R | 223858615623 | 4
C21 |  |  | 10pF | Non-polarised capacitor | CC0603_10PF_50V_5%_NP0 | 223886715109 | 1
C23, C27, C29, C37, C38 |  |  | 100pF | Non-polarised capacitor | CC0603_100PF_50V_5%_NP0 | 223886715101 | 5
C31 |  |  | 39pF | Non-polarised capacitor | CC0603_39PF_50V_5%_NP0 | 223886715399 | 1
C33 |  |  | 220pF | Non-polarised capacitor | CC0603_220PF_50V_5%_NP0 | 223886715221 | 1
C34 |  |  | 330pF | Non-polarised capacitor | CC0603_330PF_50V_5%_NP0 | 223886715331 | 1
C35 |  |  | 220nF | Non-polarised capacitor | CC0603_220NF_10V_10%_X7R | 223824615654 or CC0603KRX7R6BB224 | 1
C40, C47, C55 |  |  | 10uF | Polarised capacitor | 16TQC10M, 16TQC10M, CTE3528-21_10UF_16V_10%_LESR0800 | [NoValue], [NoValue], TPSB106K016R0800 | 3
C44 |  |  | 15pF | Non-polarised capacitor | CC0603_15PF_50V_5%_NP0 | 223886715159 | 1
C53 |  |  | 4.7nF | Non-polarised capacitor | CC0805_4.7NF_250V_10%_X7R | GRM21AR72E472KW01D | 1
C54 |  |  | 47uF | Non-polarised capacitor | C3216X5R1E476M160AC |  | 1
D1, D2 |  |  |  | Diode | ES1D |  | 2
D3 |  |  |  | Serial Diode | BAT64-04W |  | 1
IC1 |  |  |  |  | HV7360LA-G |  | 1
IC2 |  |  |  | 3-Ultra-Sound HV Switch 1=A 2=COM 3=B | MD0100N8-G |  | 1
IC3 |  |  |  |  | AD8331ARQZ |  | 1
IC4, OSC1 |  |  |  | Low-Cost, Low-Power, 8-Bit DACs with 3-Wire Serial Interface in SOT23, Resistor Set SOT-23 Oscillator 1kHz-20MHz | MAX5383EUT+T, LTC6900CS5 |  | 2
IC5 |  |  |  | DC to 6 GHz Envelope and TruPwr RMS Detector | ADL5511ACPZ-R7 |  | 1
IC6 |  |  |  | 1.5 GHz Fully Differential Amplifier | LMH6552MA/NOPB |  | 1
IC7, IC9 |  |  |  | Octal Buffer/Line Driver with 3-State Outputs | 74AC541MTC |  | 2
IC8 |  |  |  | 12-Bit, 10MSPS Sampling Analog-To-Digital Converter | AD9220ARS |  | 1
IC10 |  |  |  | Power Supply | R05-100B |  | 1
IC11 |  |  |  | Single Schmitt-Trigger Inverter | SN74LVC1G14DBVR |  | 1
J1 |  |  |  |  | 132357-11 |  | 1
J2 |  |  |  | Connector 3 Male | 1803439 (MCV 1,5/3-G-3,81) |  | 1
Jumper1, Jumper2 |  |  |  | Connector 3 Male | GRPB031VWVN |  | 2
L1, L2, L3, L4, L5, L6, L7, L8 |  |  | 75R@100MHz | Inductor | BLM21BB750SN1D |  | 8
LD1 |  |  |  | LED Green 1C 2A | LG L29K-G2J1-24-Z |  | 1
P1 |  |  | 5k | Trimming Potentiometer | 3223W-1-502E |  | 1
P8, P9 |  |  |  | Connector 46 Male | TSW-123-07-L-D-LL |  | 2
R1 |  |  | 4k7 | Resistor - 1% | R1206_4K7_1%_0.25W_100PPM | NRC12F4701TRF | 1
R2, R5, R7, R9, R18 |  |  | 10k | Resistor - 1% | R0603_10K_1%_0.1W_100PPM | NRC06F1002TRF | 5
R3 |  |  | 280 | Resistor - 0.1% | R0603_280R_0.1%_0.063W_10PPM | RN73C1J280RBTDF | 1
R4, R6 |  |  | 100 | Resistor - 1% | R0603_100R_1%_0.1W_100PPM | NRC06F4700TRF | 2
R8 |  |  | 11k | Resistor - 1% | R0402_11K_1%_0.0625W_100PPM | 232270671103L | 1
R10, R17 |  |  | 1k07 | Resistor - 0.1% | R0603_1K07_0.1%_0.063W_10PPM | RN73C1J1K07BTDF | 2
R11, R16 |  |  | 36 | Resistor - 1% | R0603_36R_1%_0.1W_100PPM | NRC06F36R0TRF | 2
R12, R14 |  |  | 536 | Resistor - 0.1% | R0603_536R_0.1%_0.063W_10PPM | RN73C1J536RBTDF | 2
R13 |  |  | 619 | Resistor - 0.1% | R0603_619R_0.1%_0.063W_10PPM | RN73C1J619RBTDF | 1
R15 |  |  | 75 | Resistor - 1% | R0603_75R_1%_0.1W_100PPM | NRC06F75R0TRF | 1
R19 |  |  | 33 | Resistor - 1% | R0603_33R_1%_0.1W_100PPM | NRC06F33R0TRF | 1
R20 |  |  | 20k | Resistor - 0.1% | R0603_20K_0.1%_0.063W_10PPM | RN73C1J20KBTDF | 1
R21 |  |  | 27k4 | Resistor - 0.1% | R0603_27K4_0.1%_0.063W_10PPM | RN73C1J27K4BTDF | 1
R22 |  |  | 40k2 | Resistor - 0.1% | R0603_40K2_0.1%_0.063W_10PPM | RN73C1J40K2BTDF | 1
R23 |  |  | 100k | Resistor - 0.1% | R0603_100K_0.1%_0.063W_10PPM | RN73C1J100KBTDF | 1
R24 |  |  | 160 | Resistor - 1% | R0603_160R_1%_0.1W_100PPM | NRC06F1600TRF | 1
SW3 |  |  |  | 4 Ways SPST DIP Switch | 1571983-4 or GDH04S04 |  | 1
TP1, TP2, TP3, TP4, TP5, TP6, TP7, TP8, TP9, TP10 |  |  |  | Test Point | C12000B |  | 10
TR1 |  |  | 1:1 | 50 Ohm 0.015 To 300MHz RF Transformers | T1-6T-KK81 |  | 1
 |  |  |  |  |  |  | 123
Approved |  | Notes

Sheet: Project Information
Project Full Path | G:\Projects\Upwork\echOpen\Altium\echOpen_ADC_Card\echOpen_ADC_Card.PrjPcb
Project Filename | echOpen_ADC_Card.PrjPcb
Variant Name | None
Data-Source Filename | echOpen_ADC_Card.PcbDoc
Data-Source Full Path | G:\Projects\Upwork\echOpen\Altium\echOpen_ADC_Card\PCB\echOpen_ADC_Card.PcbDoc
Title | Bill of Materials For PCB Document [echOpen_ADC_Card.PcbDoc]
Total Quantity | 123
Report Time | 11:40:20 PM
Report Date | 1/10/2016
Report Date & Tine | 1/10/2016 11:40:20 PM
Output Name | Bill of Materials
Output Type | BOM_PartType
Output Generator Name | BOM
Output Generator Description | Bill of Materials

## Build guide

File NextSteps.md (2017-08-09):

# Next Steps..

## Status today

 Since the end of November, where I knew nothing about electronics, I managed to learn about the following points:

* Electronics : back to the basics
* Datasheets: learning to read and understand those
* Fabs: getting to know the ecosystem, touch base with some, work an excellent agreement
* Transducers: an ongoing process.. but I do know a bit more about those.
* Documentation: getting to know more about the process of documenting open-source hardware... and getting the first automation tools on.
* A worklog: starting with the [first session with the board](/worklog/Session_1.md). Not too much a bad idea of having written it, it still has a lot of information.

## Community engaged

The results in terms of community were quite good. We managed to onboard on several media (stats as of 23/4/16):

* [HackerNews](https://news.ycombinator.com/item?id=10944617): made it to the first page for a couple of hours, 122 points, 43 comments
* [Hackaday.io](https://hackaday.io/project/9281-murgen): where the project is posted - 3.6k views, 97 followers, 25 likes so far, plus an [article](http://hackaday.com/2016/04/12/a-developers-kit-for-medical-ultrasound/).
* An [article on GeekTimes](https://geektimes.ru/post/274478/), a russian hackernews or so it seems, 11.6k views and 50 stars, with 68 comments.
* A murgen board acquired by Vanderbilt's Charles' lab.

## Leftovers

I'm now left with the following stuff to work with:
* An empty shell of a ultrasound scanner probe
* An arduino nano
* A ESP8266
* Two thermal printers
* A Raspberry 2
* Two BeagleBone Black
* A servo
* Some rapid logic invertors
* A 3.3/5V level shifter

What can I do with those?

## ToDo

We only have now to play with the following items on the next phase:

1. Playing with the design and fab the modules: 3 to go in CMS (HV/TGC/MD, enveloppe detection, SPI ADC) and 2 in stripboard mode (alim, based on the breadboard 3.3V and 5V, as well as the controler, maybe an arduino nano at first) - and start the github repo / [echOmods](https://hackaday.io/project/10899-echomods) hackaday pages as well. Work on this with Sofian and Vlad. See also the [echOmods repo](https://github.com/kelu124/echomods/).
2. Playing with an electronic emulator of the transducer - as well as an electronic model. Work on this with a partner/supplier.
3. Play with a ultrasound durable fantom. Work on this with **staticdet5** (comment on HAD). Started a [project with Virginie and Static on HAD.io](https://hackaday.io/project/11478-open-source-ultrasound-phantoms).
4. Play with the BeagleBone PRUs. Work on this with Vanderbilt.
5. Playing with some intelligent uC of FPGA. uC has my preference at first for ease of use. WifiMCU seems fun (has a 8$ STM32F411CE - 100MHz, 2.4Msps ADC, FPU, DSP instructions and WiFi to stream!) or the [Feather Wiced](https://www.adafruit.com/product/3056) (arduino IDE compatible, based on a 34$ STM32F205 ARM Cortex M3 processor running at 120MHz. Project codename would be [Croaker](https://github.com/kelu124/echomods/croaker), not created yet. Who's volunteering?

# Some resources to move further

## Bibliography

### STM32 ?
* http://www.st.com/web/en/resource/technical/document/application_note/DM00050879.pdf : How to improve ADC accuracy when using STM32F2xx and
STM32F4xx microcontrollers
* http://www.micromouseonline.com/2009/05/26/simple-adc-use-on-the-stm32/

### Working with the PRUS:
* *For low-speed comms, conventional I2C or similar protocols can be used, and there is no need to use a PRU. For high-speed comms the PRU may be extremely useful because it can service the hardware with no interruptions due to Linux context switching, and no overhead is experienced by the main ARM processor. Here are some examples that should be feasible; basically quite a few possibilities, such as interfacing to a fast ADC (e.g. analog capture)*
* http://www.element14.com/community/community/designcenter/single-board-computers/next-gen_beaglebone//blog/2013/05/22/bbb--working-with-the-pru-icssprussv2
* https://theembeddedkitchen.net/beaglelogic-building-a-logic-analyzer-with-the-prus-part-1/449 *BBB is a 100MHz logic analyzer on a BeagleBoneBlack* : Demo over the http://beaglelogic.github.io/webapp/
* http://r.git.net/beagleboard/2013-10/msg00204.html : can the PRU be used to interface the Beaglebone to external ADC? I need to capture 500 micro-seconds of data at a 5 MHz rate? -> It depends on the interface to the ADC. There is a parallel capture interface that will easily run that fast, and you may be able to use the bit-shift interface to do serial or something like SPI if the PRU's capability lines up with what your ADC wants to see.
* http://www.element14.com/community/community/designcenter/single-board-computers/next-gen_beaglebone//blog/2013/08/04/bbb--high-speed-data-acquisition-and-web-based-ui : In its current state, it grabs analog data from an ADC, and dumps it into memory on the BBB, ready to be displayed or further processed. It could be used for gathering analog information from sensors, CCDs or other data acquisition use-cases. To be reasonably useful, **the desire was for it to support 20Mbytes/sec of data or more**. It does achieve this, but it is for further study to find higher speed methods.  Once the data has been captured (2000 samples in this example), the command byte is acknowledged, so that the Linux hosted application can know that the PRU has completed. The PRU now sits and waits for a new instruction from the Linux hosted application. **-> works for us - fixed depth = fixed # of samples**
* http://exploringbeaglebone.com/chapter13/#The_ADS7883_Single-Channel_12-bit_ADC_1MSps_max
* 5Msps -> Parallel -> PRU up to 12 bits -> can go further than 5Msps (SOA) 

* https://hackaday.com/2014/06/22/an-introduction-to-the-beaglebone-pru/
* https://www.embeddedrelated.com/showarticle/603.php
* https://www.embeddedrelated.com/showarticle/586.php
* https://github.com/beagleboard/am335x_pru_package

**http://stackoverflow.com/questions/35939058/beaglebone-without-dac-from-digital-to-analog-converter
**http://stackoverflow.com/questions/35910431/getting-beaglebone-prus-to-work-using-pasm

### WebRTC

* awesome stuff at https://rtc.io/ for nodejs + webrtc

### PCBs
* Another supplier : seeedstudio.com(reco by F&V), see also http://pcbshopper.com/

* PCBA abroad : myropcb, nortechsys. SeeedStudio does only north america in fab-mode

* PCBA in france: Quad Ind, and PCB-Pool

### Caracterization of the piezos:

Caractérisation du piezo :

* http://www.biosono.com/PrmtLgd/PrmtLgd.php?id=TrnsRlc
* http://www.brl.uiuc.edu/Downloads/bigelow/APPENDIX%20C.PDF ou en local sur : File:APPENDIX C.PDF
* http://www.vtvt.ece.vt.edu/research/papers/08sas.pdf ou en local sur : File:08sas.pdf

## Documentation tools and processes

Still a work in progress... but the key here is to move towards a maximum of automation. No other solution.

## Fun stuff

Using the Pi as an oscilloscope:
* [Is Pi powerful enough for an oscilloscope project?](http://raspberrypi.stackexchange.com/questions/4129/is-pi-powerful-enough-for-an-oscilloscope-project)
* [Raspberry Pi as an Oscilloscope @ 10 MSPS](https://digibird1.wordpress.com/raspberry-pi-as-an-oscilloscope-10-msps/)

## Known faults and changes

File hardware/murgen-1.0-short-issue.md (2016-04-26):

Murgen 1.0 short circuit
===

25/02/2016: we received the boards, all seems good.

However, we realised there was a short circuit between 5V and GND, and not between 3.3V and GND (thanksfully !) 

TL;DR:
* There was a short
* We found that the RECOM was inverted -- to be amended for the 1.1
* Identified a possible short...
* Let's see !

## Transcript of the chat

>[2/26/2016 12:15:58 AM] Sofian: Of course it will be the mistake of the designer :smile: I have made a mistake with the Power supply module footprint, I have created it flipped, because I should have paid better attention to the datasheet
>
>[2/26/2016 12:17:53 AM] Sofian: The numbers of the pins show the bottom view and not top view, I have created it as a top view, this can still be solved by removing the power supply module and installing it from the bottom side, I am very sorry for this mistake, but I am not entirely sure it would create the short though, unless you have provided 5 volts to it.
>
>[2/26/2016 12:26:35 AM] Sofian: This is one possible location where a solder joint might happen between GND and 5V

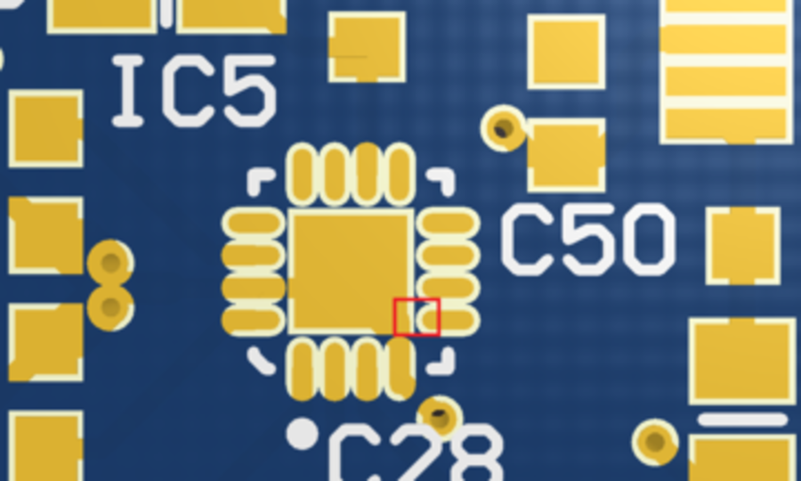
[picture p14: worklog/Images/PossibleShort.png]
Possible short


>
>[2/26/2016 12:43:19 AM] Sofian: GND points
 
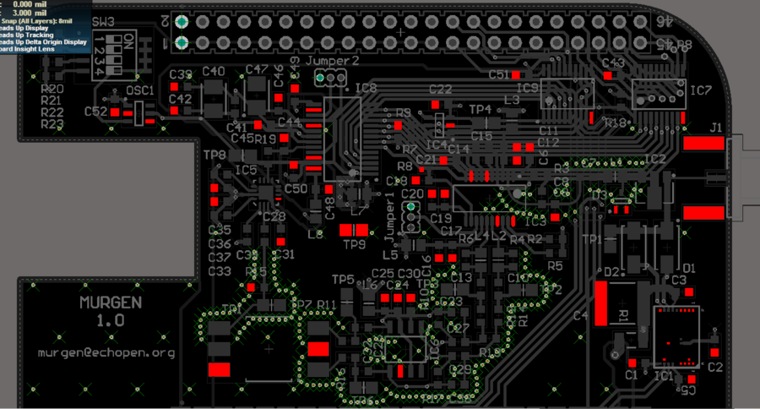
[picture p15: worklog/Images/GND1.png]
GND Points 1

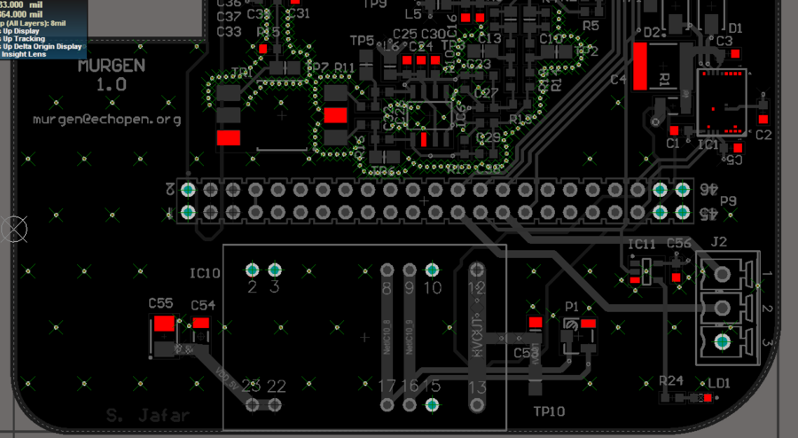
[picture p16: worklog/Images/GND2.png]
GND Points 2

 
>[2/26/2016 12:45:39 AM] Sofian: VDD_5V
 
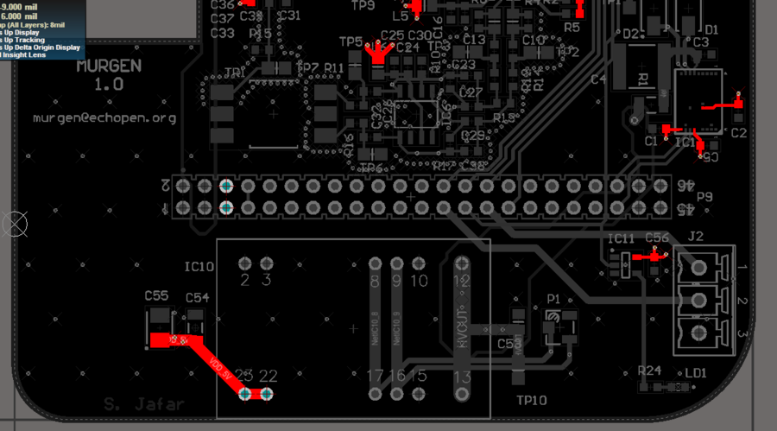
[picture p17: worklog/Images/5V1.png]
5V Points 1

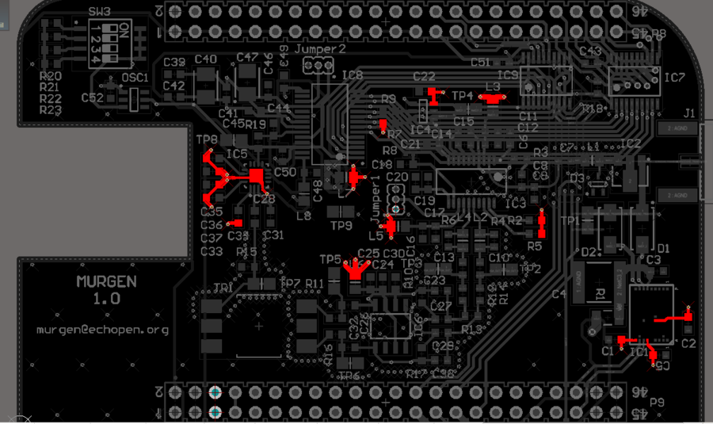
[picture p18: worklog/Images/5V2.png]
5V Points 2

 
>[2/26/2016 1:14:33 AM] Sofian: This excel file contains the settings for the switch settings, it allows you to set various frequencies for sampling from 1MHz to 12MHz, which is not supported, so you can go upto around 9MHz with the selection I have given you.
>
>[2/26/2016 1:23:22 AM] Sofian: As for setting the voltage: First measure resistance between GND and Pin8 on the DC/DC module, adjust the pot until this value is zero Ohm
>
>[2/26/2016 1:23:46 AM] Sofian: Also make sure the value between pin 8 and pin 9 on the DC/DC module is around 5kOhm
>
>[2/26/2016 1:25:06 AM] Sofian: Please make sure of this many times, refer to the datasheet of the DC/DC module to make sure the pins you are checking are correct
and don't forget to flip the DC/DC module to the bottom side

>[2/26/2016 1:26:07 AM] Sofian: I hope you have not powered it, I also recommend that once you remove the DC/DC module you check the short again to make sure it went away or not, maybe the source is not the DC/DC module
>
>[2/26/2016 1:28:19 AM] Sofian: TP9 is GND pin by the way
>
>[2/26/2016 1:49:27 AM] Sofian: I also checked all other foorprints and pinouts to make sure I have no other mistakes, I could not find any

## Action

**Flipping the RECOM !**

## Resources

 * [murgen](https://github.com/kelu124/murgen-dev-kit) for the original board

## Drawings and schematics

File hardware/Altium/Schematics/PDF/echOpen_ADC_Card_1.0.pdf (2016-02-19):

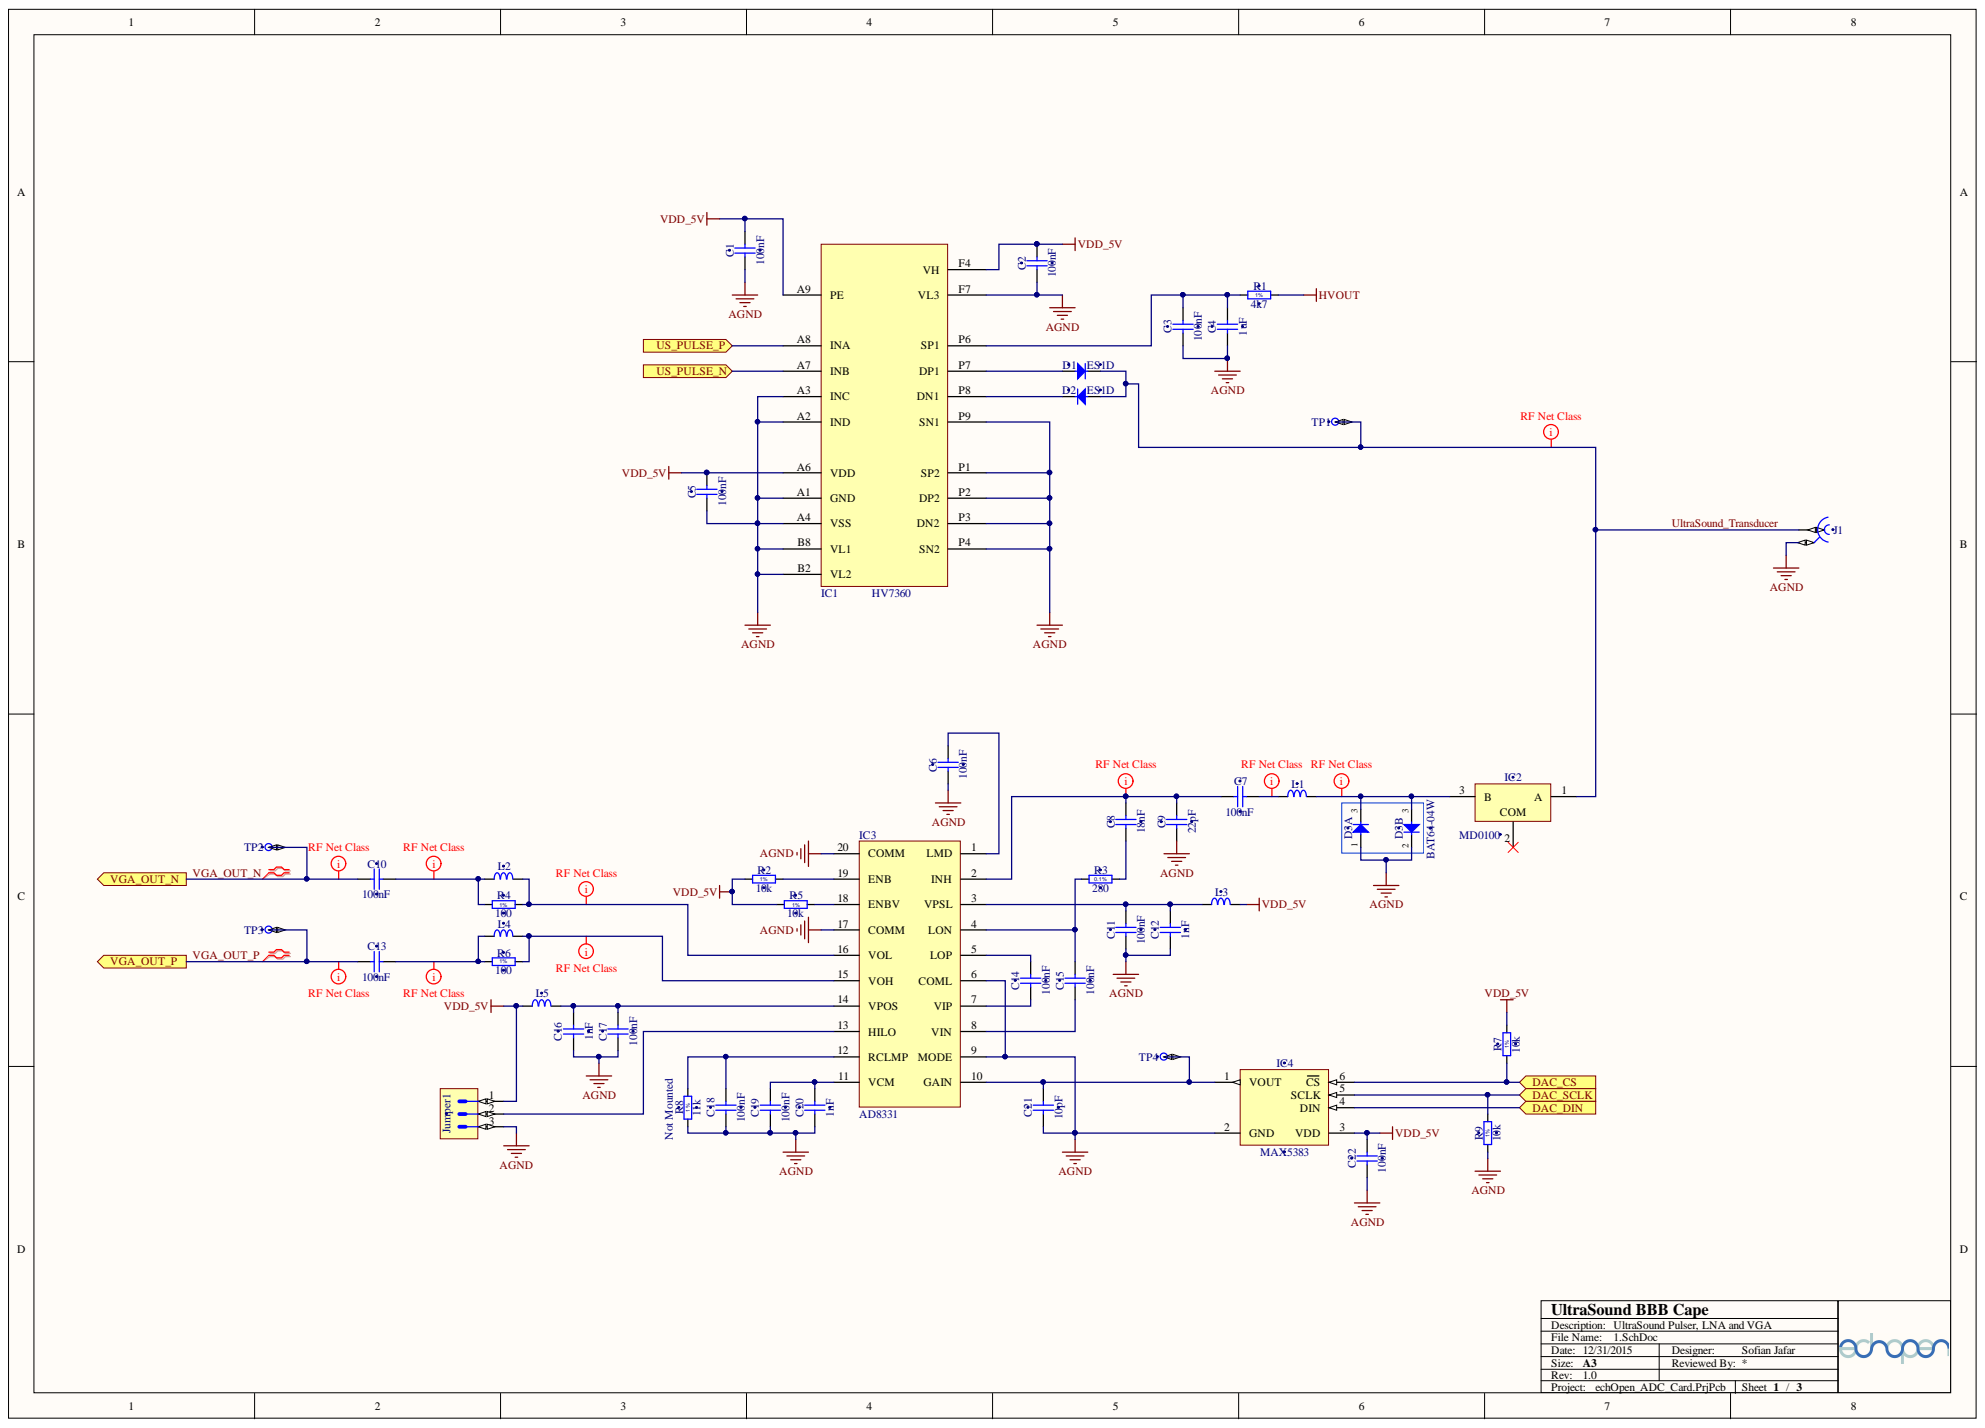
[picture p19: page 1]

UltraSound BBB Cape
Description: UltraSound Pulser, LNA and VGA
File Name:

Date: 12/31/2015 | Designer: Sofian Jafar
Size: A3 | Reviewed By: *
Rev: 1.0
Project: echOpen_ADC_Card.PrjPcb | Sheet 1 / 3

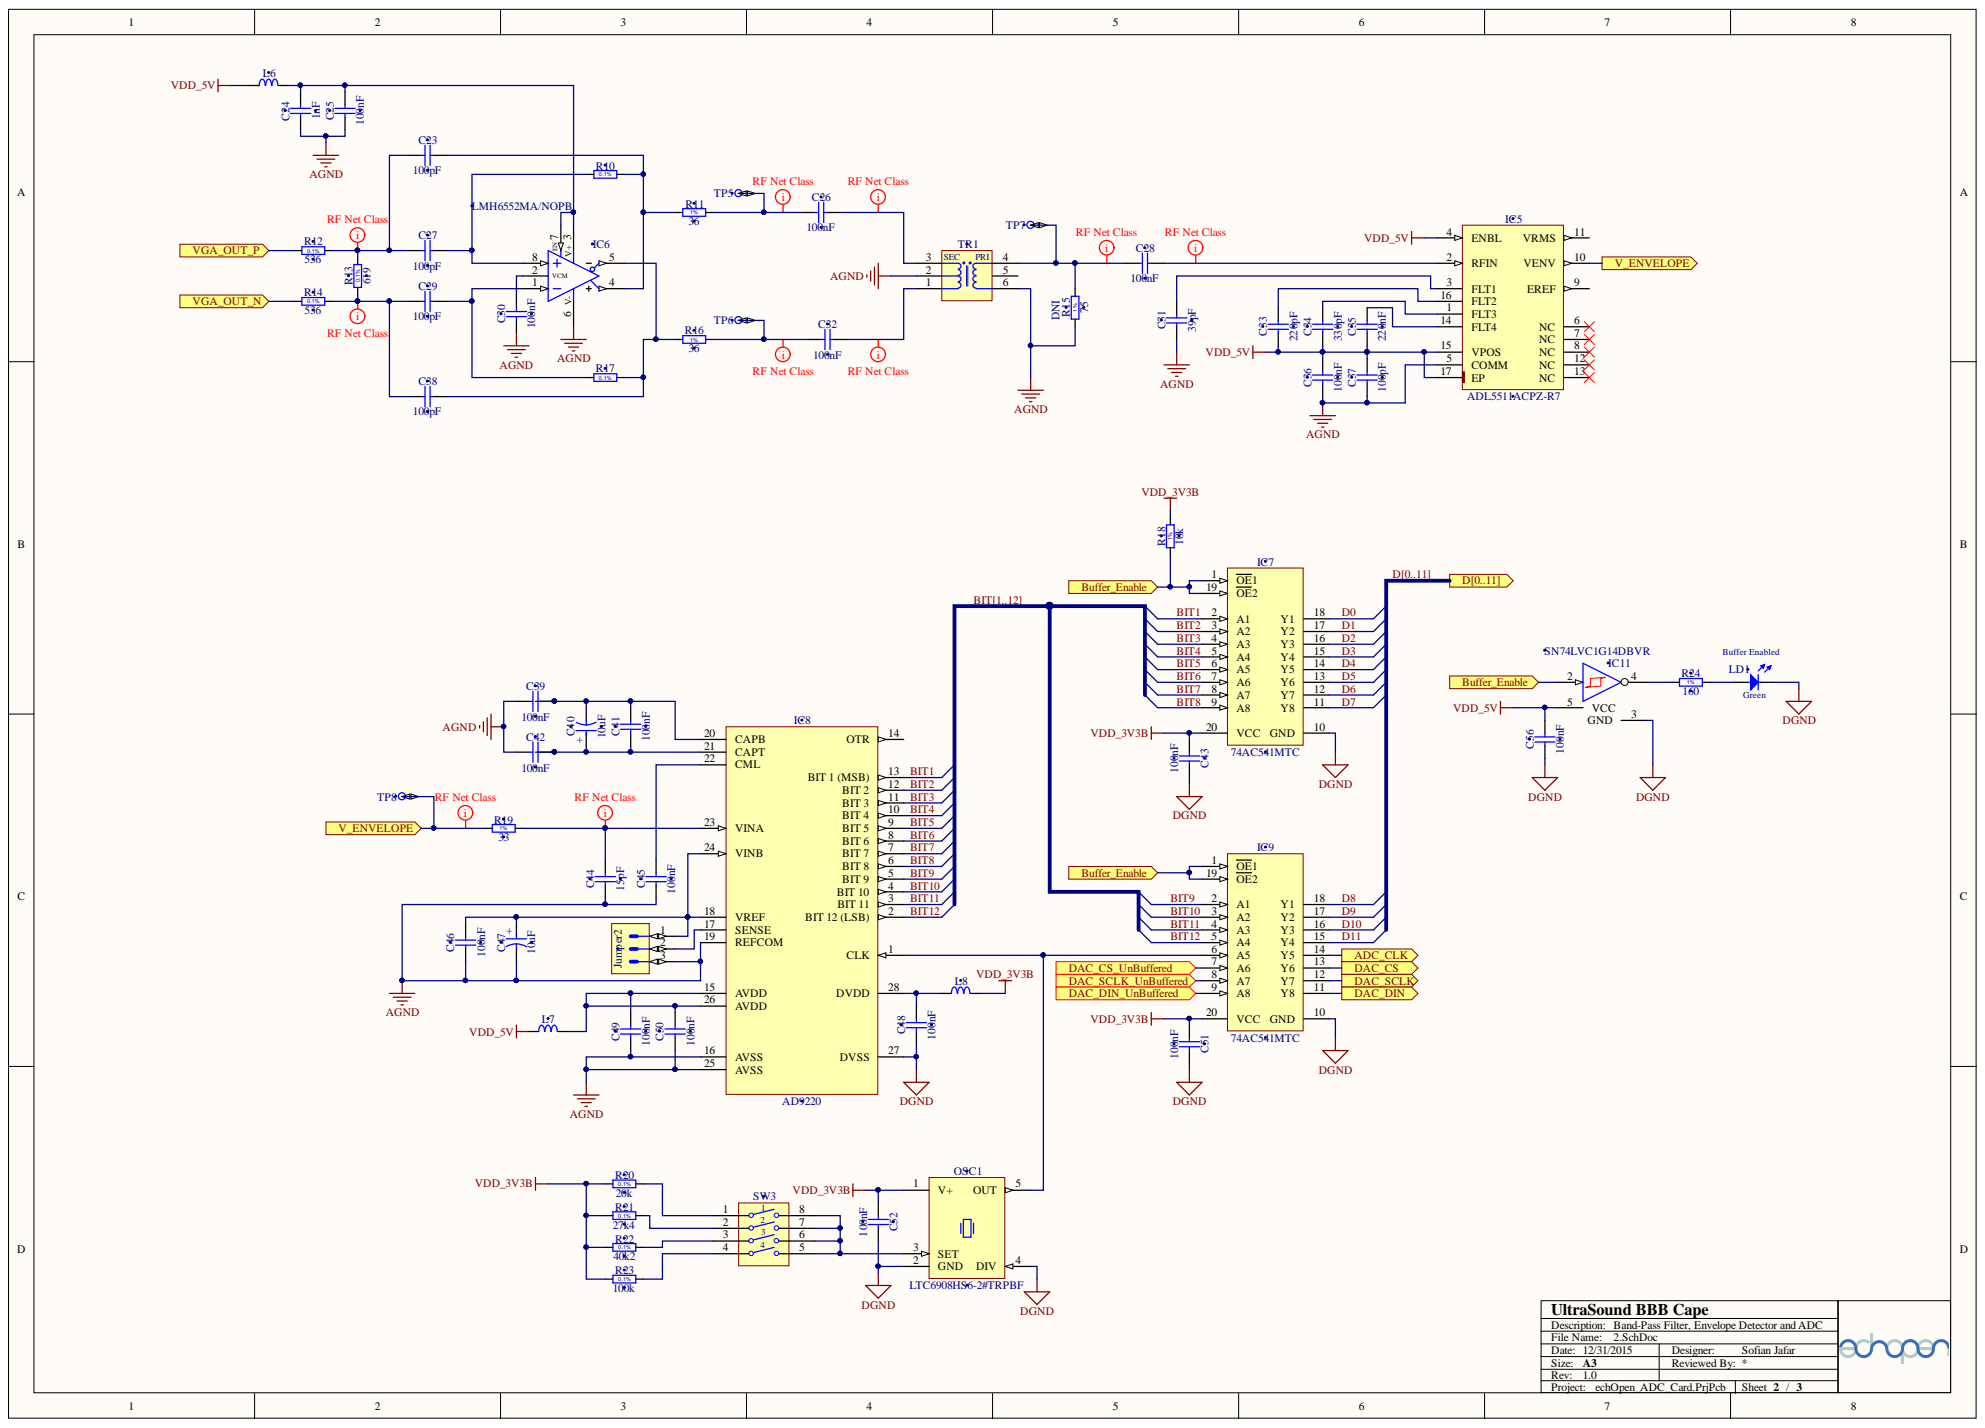
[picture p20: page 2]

LMH6552MA/NOPB | 0.1% IC6 5

UltraSound BBB Cape
Description: Band-Pass Filter, Envelope Detector and ADC
File Name:
Date:

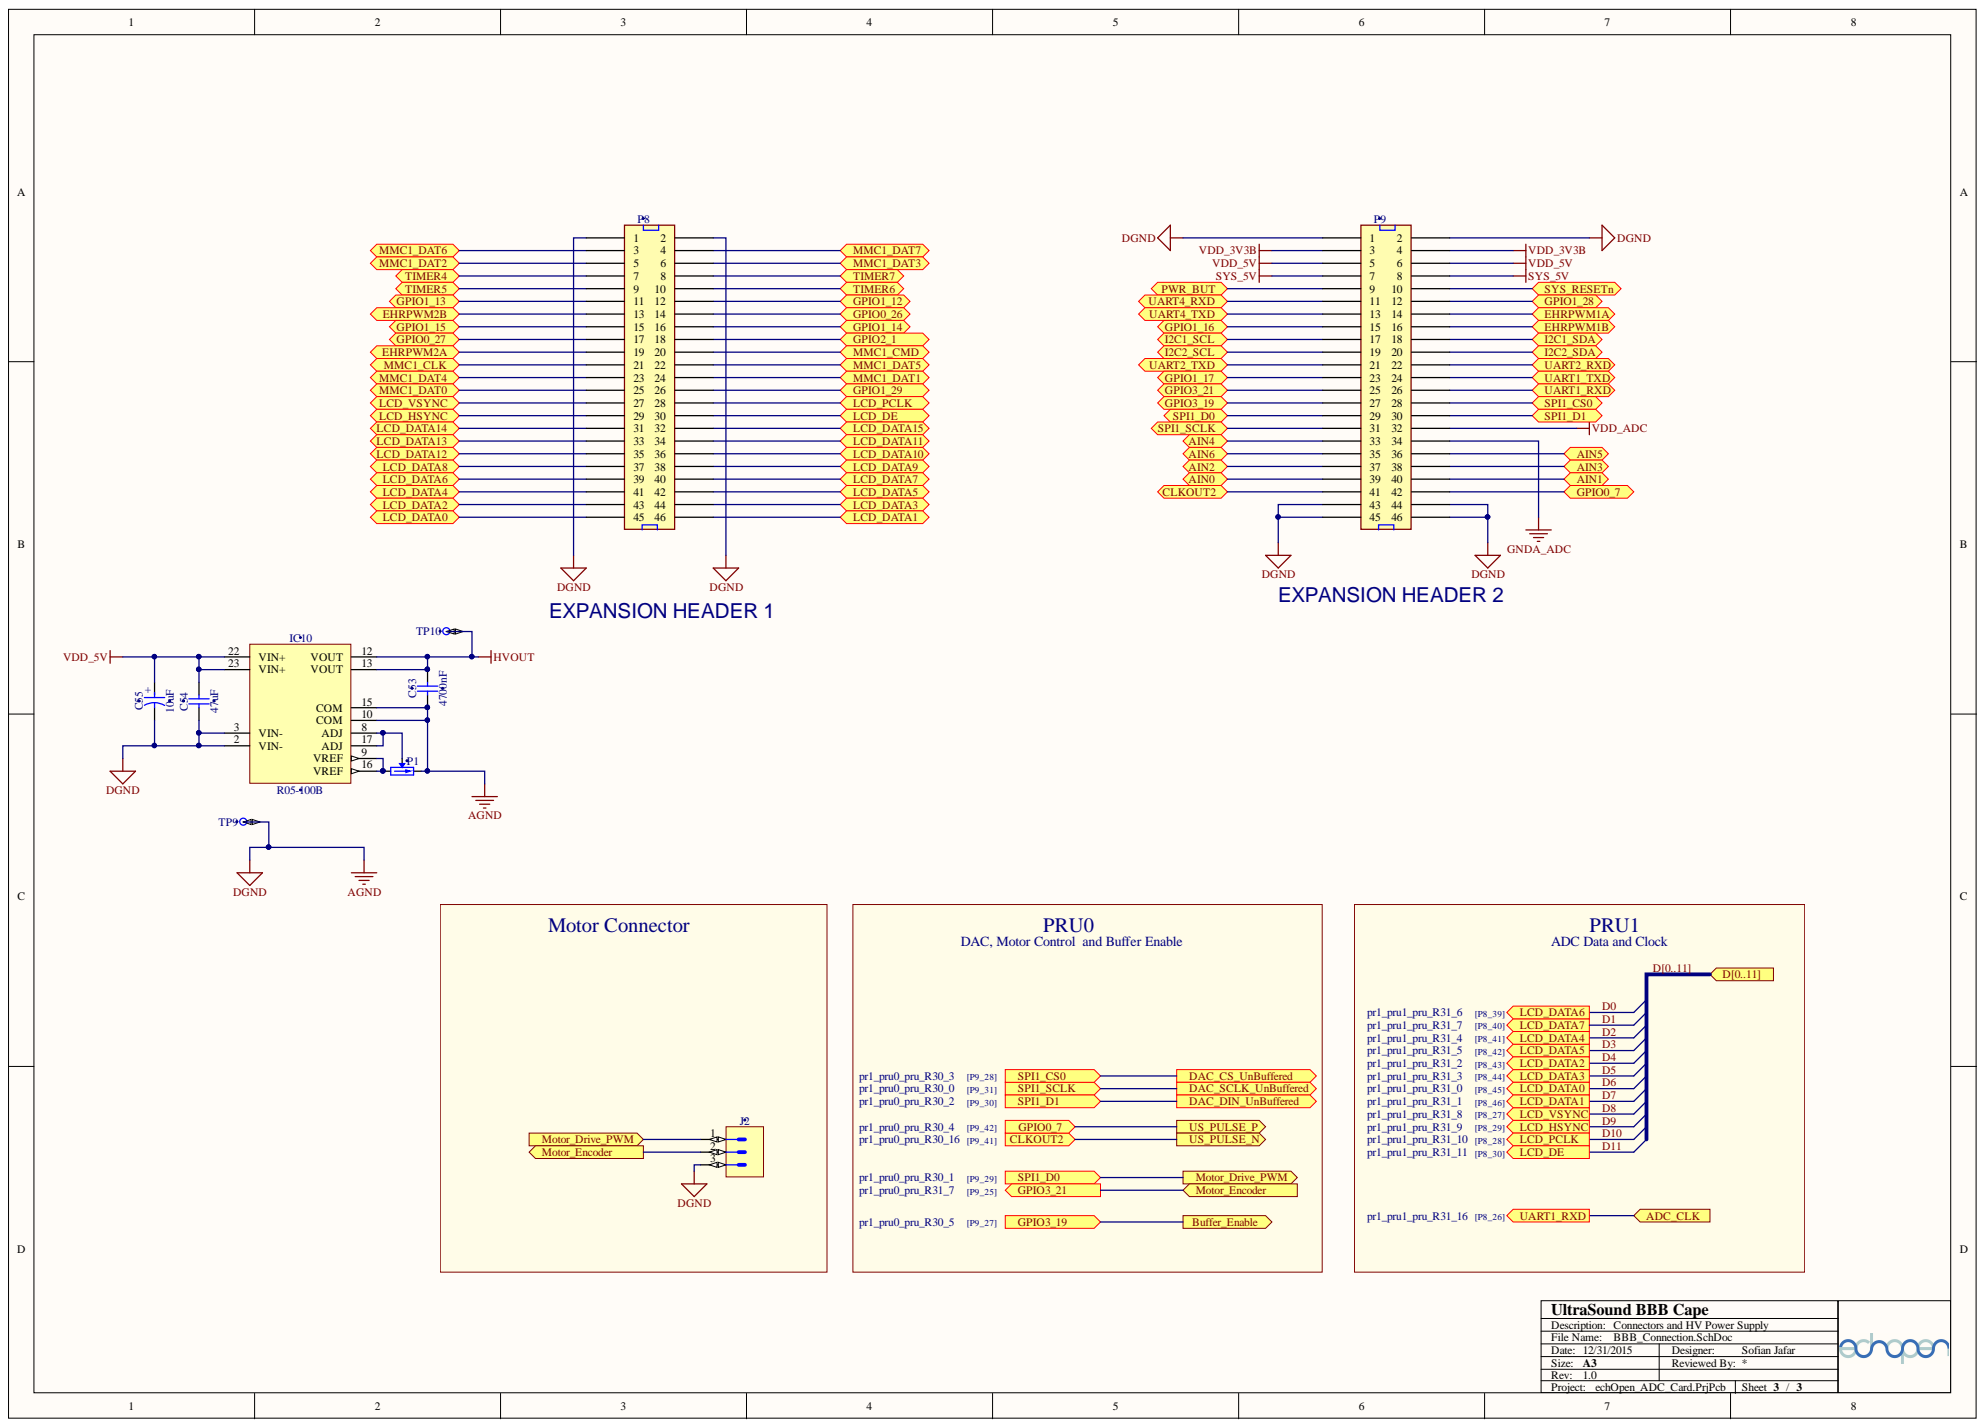
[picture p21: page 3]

UltraSound BBB Cape
Description: Connectors and HV Power Supply
File Name:
Date:

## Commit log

2016-02-21 Updating bibliographie and Readme - especially on HV
    [echOpen_ADC_Card_1.0_BOM.xls]
2016-02-26 Documentation for the Murgen short circuit
    Upload of images
2016-02-26 Documenting short issues and board debug
2016-04-03 Release cleaning ongoin
    [1.SchDoc, 2.SchDoc, BBB_Connection.SchDoc, Bill of Materials-echOpen_HV+Pulser_Board.xls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]
2016-06-16 Old repo of Goblin and tobo removed
    [1.SchDoc, Bill of Materials-echOpen_HV+Pulser_Board.xls, Pick Place for echOpen_HV+Pulser_Board.csv, echOpen_HV+Pulser_Board.GBL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]
2016-06-21 Scan conversion for images taken with Murgen board
    Data from the Murgen board was collected in MATLAB, but the code for
    scan conversion is in Python.
    Noise reduction was done by returning the absolute value of the output
    to remove negative noise and then a log greyscale was implemented.
2016-06-23 June 22, 2016
    Today I got the Beaglebone to pulse the the Murgen board to get images
    (Gain voltage of 0.7V and current of 0.086A). Beaglebone sends the
    positive and negative pulses from P9_22 and 21 respectively. I worked
    on the software side of image processing, implementing a high pass
    filter, hilbert transformation, and scan conversion. Data, codes, and
    images are included.
    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
2016-06-24 Echoes at various TPs
    I went through various TPs today, measuring between them to try to see
    how the signal was processed by the Murgen board. I was expecting an
    envelope at TP8, but it only seemed to give me the same signal as
    between TP2 and TP3, but with less gain.
2016-06-25 Removing the filter part for murgen
2016-07-26 New test of probes
    [20160721-094817.csv, 20160721-095621.csv, 20160721-095715.csv, 20160721-095804.csv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]
2016-08-02 Pic of shorting the filter

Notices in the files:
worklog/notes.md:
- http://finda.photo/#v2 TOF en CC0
